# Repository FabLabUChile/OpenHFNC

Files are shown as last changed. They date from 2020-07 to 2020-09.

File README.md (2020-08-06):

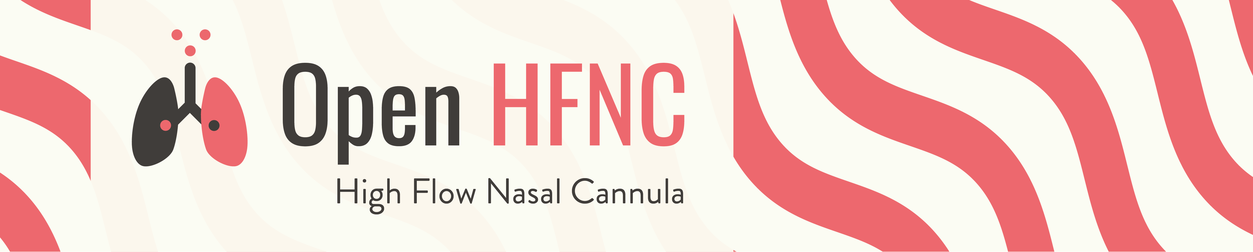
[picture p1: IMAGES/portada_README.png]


# OpenHFNC, Low-Cost Open-Source Alternative Device for High Flow Nasal Therapy
Open Source High Flow Nasal Cannula (Sistema de Terapia Nasal de Alto Flujo de Código Abierto) 

Last update 2020/07/09

### WARNING/DISCLAIMER: We cannot recommend the use of this device on medical applications since it has not been extensively proven. In this project our focus is on reporting the current performance of the device and sharing knowledge that can be used for the development of alternative equipment that can be used in the context of COVID 19. At the current stage this device does not meet all all technical requirements, however we meet some technical requirements that are important. Any further development must be acompanied with the supervision of medical experts. There is a significan risk associated with the inapropiate use of any medical equipment and precautions must be followed. 

Acknowledgements: We thank the collaboration of many profesionals, specially those from the Hospital Clinico Universidad de Chile and also expert advice from professionals from the Pontificia Universidad Catolica de Chile. Through the development of this project we have shared experience and knowledge about the funcioning of several components. 

### ADDITIONAL WARNINGS: This device has not been tested to meet any FDA regulation and has not been certified. 

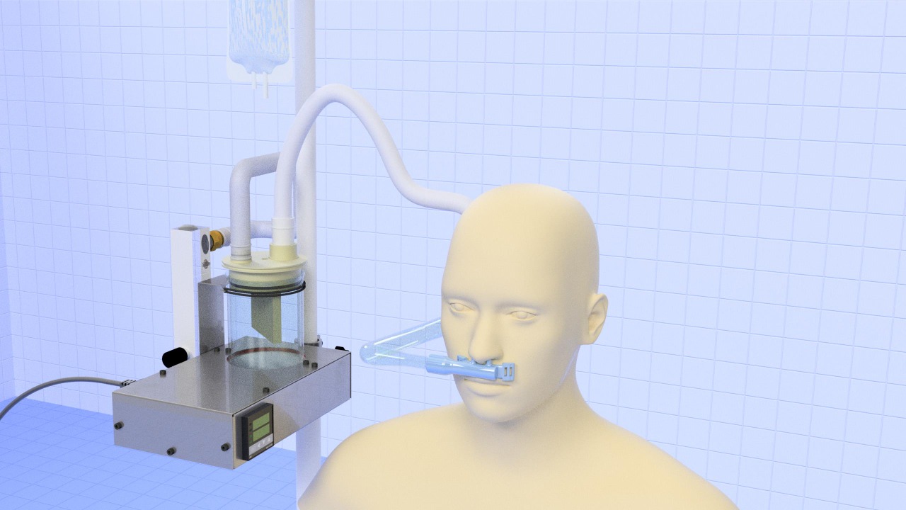
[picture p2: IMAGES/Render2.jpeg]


### MOTIVATION

High Flow Nasal Therapy is an alternative treatment for CODVID 19 patients. Implementing a HFNT device seems less complicated and less expensive than implementing a mechanical ventilator. Moreover it has been reported that HFNT produces less colateral damage to lungs and is also linked with better recovery. 

### TECNICAL REQUIREMENTS

R1. Adjustable Air Flow (Flujo regulable de aire).

The air flow should be in the range of 50 to 70 L/min. 

R2. Mixing Air and Oxygen (Mezcla de Aire y oxígeno en forma regulada).

It should be possible to mix air and oxygen and to regulate the flow of both. Different levels of FiO2 should be
attained. 

R3. Humidification (Humidificación)

Air reaching the patient must be humidified (RH 100%, AH 84 mg/L)

R4. Temperature (Temperatura)

Air must be pre-heated and should reach the patient at a temperature or 37 degrees C. 

R5. Use of heated tube (Uso de tubo calefaccionado)

A pre heated tube must be used to prevent condensation. 

R6. Nasal Cannula (Cánula nasal)

Include a nasal cannula. 

R7. Rapid fabrication.

Implemented ASAP.

R7. Scalability

Several units must be produced. 

### FILE STRUCTURE

* CAD: Design Files of Components.

* BOM: Bill of Materials. 

* ASI: Assembly Instructions. 

* UMA: User Manual. 

* TEC: Technical Evaluation of Performance

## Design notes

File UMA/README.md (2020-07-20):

# USER MANUAL

More information about Instructions for Use DENTAL SG Resine from Formlabs [HERE](https://s3.amazonaws.com/servicecloudassets.formlabs.com/media/Materials/Formlabs+Materials/115000015710-Using+Dental+SG+Resin/DentalSG-Instructions-for-use.pdf)

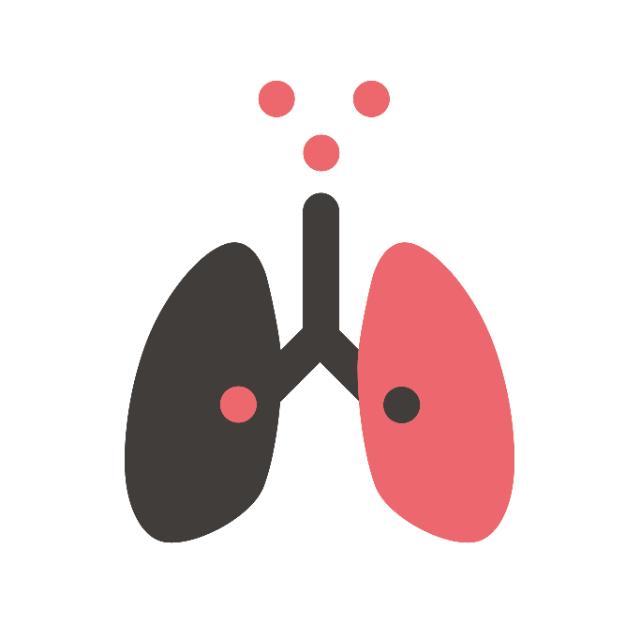
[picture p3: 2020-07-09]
IMAGES/OpenHFNC.jpg

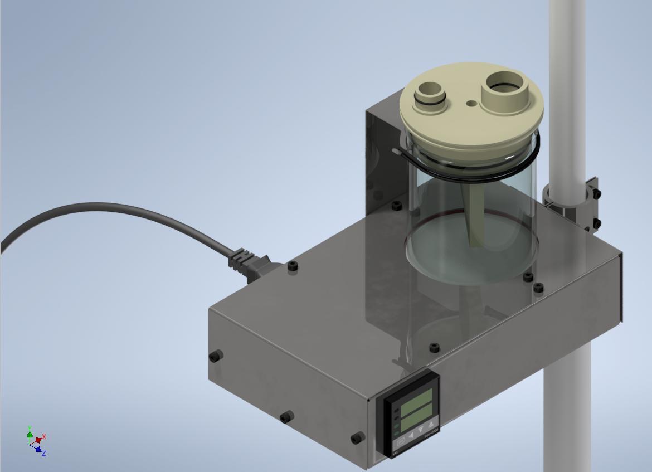
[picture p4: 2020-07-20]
IMAGES/Render1.jpg

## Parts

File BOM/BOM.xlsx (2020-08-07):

Open HFNC | Bill of Materials
System | Subsystem | Part | Quantity | Material | Manufactured or COTS | Description | Reference Sheet in OpenHFNC Manufaturing Drawings |  | COTS - International
Heating-Box | Heating plate box | Box base | 1 | Steel Carbon 1mm thickness | Manufactured | Base of the box that contains the parts that allow the heating of the heating plate and the beaker glass. | Sheet 2 and 3 - DXF file
 |  | Box top | 1 | Steel Carbon 1mm thickness | Manufactured | Cover of the box that contains the parts as descripted above. | Sheet 2 and 4 - DXF File
 |  | M4 rivet nut | 14 |  | COTS | Rivet nut on box base used for linking it with the cover trough the DIN912 M4x10 Screw |  |  | https://www.mcmaster.com/95105A167/ (PENDIENTE, NO ES LA MISMA)
 |  | Heating plate | 1 | Duraluminum | Manufactured | Cirucular plate that receives the heating resistance, distributing the heat, mainly in one of his faces where the beaker glass stands.. | Sheet 2 and 7
 |  | Oring 2-343 Silicone | 1 | Silicone | COTS | Seal that isolates thermal conduction from the heating plate to the top box. Also functions as water leak seal.
 |  | Heater fixing bar | 1 | Alumin | Manufactured | Aluminium bar (125x12x1). Functions as supporting link between the heating plate and the top box. | Sheet 2 and 7
 |  | DIN912 M4x0.7x40-8.8 socket head screw | 2 |  | COTS | DIN912 M4x0.7x40-8.8 socket head screw Holds heater fixing bar to box top |  |  | https://www.mcmaster.com/91290A184/
 |  | DIN 934 M4x0.7 nut | 2 |  | COTS | DIN912 M4x0.7 Nut - Holds heater fixing bar to box top |  |  | https://www.mcmaster.com/90592A090/
 |  | DIN912 M4x0.7x10-8.8 socket head screw | 10 |  | COTS | DIN912 M4x0.7x10-8.8 socket head screw - Secures Box base to box top fitting itself in to M4 Rivet Nut |  |  | https://www.mcmaster.com/91290A144/
 | Electric parts | Thermo couple | 1 |  | COTS | Thermocouple Type K M6 Thread. Measures temperature from Heating plate, REXC100 controller reads it. |  |  | https://www.mpja.com/Thermocouple-Type-K-M6-Threaded-Tip/productinfo/32106%20MI/
 |  | Heater 630W | 1 |  | COTS | Cartridge heater, 220V - 630W. 5/8' DIamater 3' Long. Converts electrical energy in to heat |  |  | https://www.mcmaster.com/35025K473/ (NOTA: IDEALMENTE 630W)
 |  | REXC100 controller | 1 |  | COTS | PID temperature controller.Adjustable Setpoint 0 - 400ºC |  |  | https://www.mcmaster.com/38615K73/ https://www.amazon.com/-/es/REX-C100-48-100-controlador-temperatura/dp/B07KXPLZTQ
 |  | Solid State Relay SSR-25DA | 1 |  | COTS | Solid State Relay; controls current flow to Heater 630W (opening it or closing it) in response to the REXC100 signal |  |  | https://www.amazon.com/Artshu-M%C3%B3dulo-SSR-25DA-entrada-24-380VAC/dp/B07JZF6973/
 |  | On-Off Switch | 1 |  | COTS | On/Off switch for electrical energy, from OpenHFNC team. |  |  | https://www.mcmaster.com/7030K45/
 |  | IEC C14 male panel connector | 1 |  | COTS | C14 male power connector |  | https://altronics.cl/conector-poder-panel-macho-c14?tag=C14 | https://www.amazon.com/Baomain-Panel-Power-Socket-Connector/dp/B00WFYS1HS
 |  | 220 AC power cable | 1 |  | COTS | 220 AC power cable- C14 female power connector |  |  | https://www.mcmaster.com/power-cords/voltage~250v-ac/
 |  | DIN913-M5x5 socket screw flat end | 2 |  | COTS | DIN 913-M5x5 socket screw flat end-Sets heating cartridge to heating box |  |  | https://www.ametric.com/product/85223/m5x5-din-913
 |  | DIN7991 M3x0.5x10-8.8 countersunk head cap screws | 2 |  | COTS | DIN 7991 M3x0.5x10-8.8 countersunk head cap screw.Sets panel connector C14 to top box |  |  | https://www.mcmaster.com/91294A130/
 |  | DIN 934 M3 nut | 2 |  | COTS | DIN934 M3x0.5 nut. Sets Panel C14 power connector to top box. |  |  | https://www.mcmaster.com/90592A085/
 | Glass vase & flow meter fixer | Glass fixer plate | 1 | Steel Carbon 1mm thickness | Manufactured | Plaque that is set to heating plate and allows the beaker glass and the flowmeter to stay in place. | Sheet 2 and 5 - DXF file |  | -
 |  | DIN912 M4x0.7x10-8.8 socket head screw | 2 |  | COTS | DIN912 M4x0.7x10-8.8 socket head screw - Sets the glass fixer plate to the heating box. |  |  | https://www.mcmaster.com/91290A144/
 |  | Oring 2-159 | 1 | Nitrile | COTS | Oring that functions as elastic band between beaker glass and the glass fixer plate.
 | IV stand fixer | IV stand fixer plate | 2 | Steel Carbon 1mm thickness and A53 Pipe | Manufactured | Plaque that is set to the heating box and allows in his other end to be fixed to the IV stand. | Sheet 2 and 6 - DXF file
 |  | Star knob 1/4 UNC | 1 |  | COTS | Star Knob 1/4-20UNC. For stand fixer plate to IV stand fixation |  |  | https://www.amazon.com/Big-Horn-19707B-5PK-Star-Thru/dp/B01DO22H5Q?c=ts&s=industrial&ts_id=16412791
 |  | DIN912 M4x0.7x10-8.8 socket head screw | 6 |  | COTS | DIN912 M4x0.7x10-8.8 socket head screw - (4) are for setting the stand fixer plate to heating box. (2) are for attaching both stand fixer plates. |  |  | https://www.mcmaster.com/91290A144/
 |  | DIN 934 M4 nut | 2 |  | COTS | DIN 934 M4x0.7 Nut.Used for attaching both stand fixer plates. |  |  | https://www.mcmaster.com/91415A020/
 |  | Split washer DIN 124B D4 | 2 |  | COTS | DIN 124B Split Washer Inner diameter 4mm.Used for attaching both stand fixer plates.
Ventilation pipeline | Flow pipelines | LZM-15ZT flowmeter | 1 |  | COTS | Flowmeter 10-100 LPM (0.6-6 m3N/h) - Conections G1/4 BSP female and G1/2 BSP male, both for inlet and outlet |  |  | https://www.grainger.com/product/BROOKS-10-to-100-lpm-Variable-Area-16X857
 |  | Corrugated tube | 1 |  | COTS | Tube that carries air/oxygen flow from flowmeter to the beaker glass.
 |  | Heated tube | 1 |  | COTS | Heated tube that carries air/oxygen humidified flow from beaker glass to transfer tube. |  |  | https://www.directhomemedical.com/HBT300-hybernite-heated-cpap-hose-tube.html
 |  | Transfer tube | 1 |  | COTS | Tube that carries air/oxygen flow from heated tube to nasal cannula. .Also serves as flow area smooth reduction tube between the components at his ends. |  |  | https://www.amazon.com/Hand-Drum-Pump-Siphon-Polyethylene/dp/B00ZZY2EFU Dukshin, Siphon Hand Pump (Product Number: DP-14)
 |  | Conical rubber stopper 12mm | 1 |  | COTS | Rubber stopper (9,5×12,5-17,5). Plug a hole of transfer tube to adapt this item for ventilation pipeline |  |  | https://www.mcmaster.com/9545K113-9545K11/
 |  | BSP 1/4 - Hose 7/8 | TBD |  | COTS | Fitting Connection between flowmeter output and corrugated tube
 |  | BSP 1/4 - Hose 1/4 | TBD |  | COTS | Fitting Connection between 1/4' high flow medical tube and flowmeter input |  |  | https://www.mcmaster.com/1075T22/
 |  | Y conection | TBD |  | COTS | Y connector that receives air and oxygen and delivers to both 1/4' high flow medical tubes.
 |  |  | TBD |  | COTS
 | Beaker glass - Top connectors | Beaker glass 600ml, diam: 90mm | 1 |  | COTS | Beaker Glass 600ml diameter 90mm. For distilled water. Receives heat coming from the heating plate.Where water evaporation for air/oxygen flow humidification occurs. |  |  | https://www.duran-group.com/en/produkte-loesungen/laborglas/produkte/kochglaeser-allgemeines-laborglas/becher.html - Cat. No.: 21 106 48
 |  | Top lid body | 1 | Polypropylene | Manufactured | Beaker glass top lid body. Seals the gaps and create connections for the heating tube (oulet flow) and corrugated tube (inlet flow) | Sheet 8 and 9
 |  | Heated tube-top lid connector | 1 | Polypropylene | Manufactured | Connector between heating tube and top lid body. | Sheet 8 and 10
 |  | Corrugated tube-top lid connector | 1 | Polypropylene | Manufactured | Connector between corrugated tube and top lid body | Sheet 8 and 10
 |  | Paddle | 1 | Polypropylene | Manufactured | Paddle that provides separation inside the beaker glass and allows the entering flow to moisturize by forcing it to pass near water in evaporation process . | Sheet 8 and 11
 |  | DIN 912 M4x16 | 1 | Stainless steel | COTS | DIN912 M4x0.7x40-8.8 socket head screw -Sets Paddle to Top Lid Body |  |  | https://www.mcmaster.com/91290A154/
 |  | Oring 2-007 | 1 | Nitrile | COTS | Seal between paddle and top lid body
 |  | Oring 2-018 | 1 | Nitrile | COTS | Seal between corrugated tube amd top lid connector
 |  | Oring 2-019 | 1 | Nitrile | COTS | Seal between corrugated tube-top lid connector and top lid body
 |  | Oring 2-022 | 1 | Nitrile | COTS | Seal between heated tube-top lid connector and heated tube
 |  | Oring 2-026 | 1 | Nitrile | COTS | Seal between heated tube-top lid connector and top lid body
 |  | Oring 2-151 | 1 | Nitrile | COTS | Seal between top lid body and beaker glass
 | Nasal cannula | Nasal cannula body | 1 | Dental SG Resin | Manufactured | BIocompatible 3D printed nasal cannula Delivers humidified air/oxygen flow to the patient through his nostrils. | STEP and STL File
 |  | Oring 2-014 | 1 | Nitrile | COTS | Seal between nasal cannula body and transfer tube
 |  | Elastic band | TBD how many meters |  | COTS | Elastic band used to hold nasal cannula to the patients head.

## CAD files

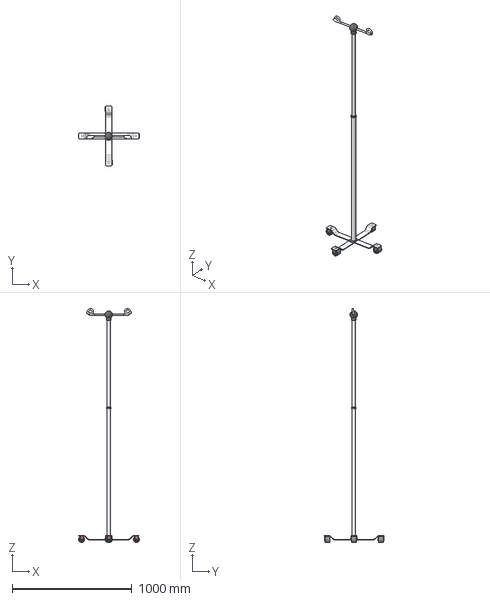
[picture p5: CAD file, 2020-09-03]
CAD/Step/Auxiliary Components/IV Stand.stp
508.6 x 502.9 x 1955.7 mm

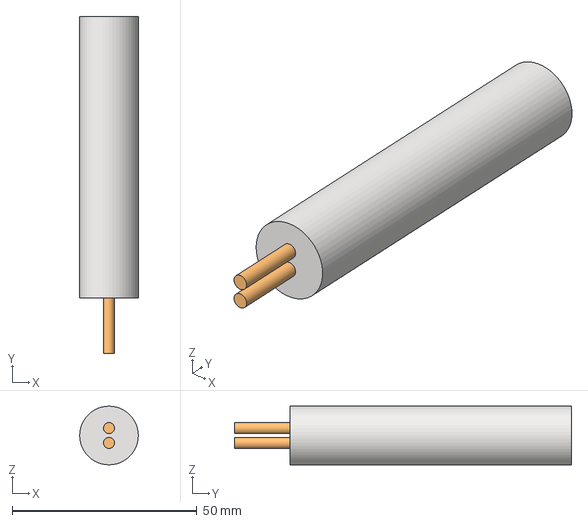
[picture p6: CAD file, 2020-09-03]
CAD/Step/Heating Box/Electric Parts/Heater630W.stp
15.9 x 91.2 x 15.9 mm

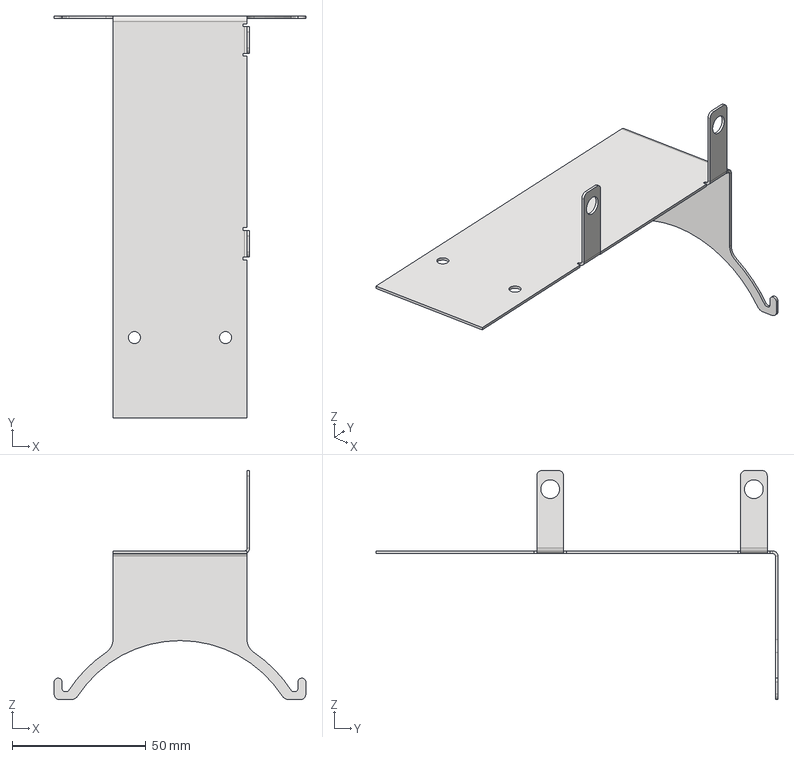
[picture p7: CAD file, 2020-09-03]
CAD/Step/Heating Box/Glass vase _ flow meter fixer/Glass fixer plate.stp
93.9 x 150.0 x 85.5 mm

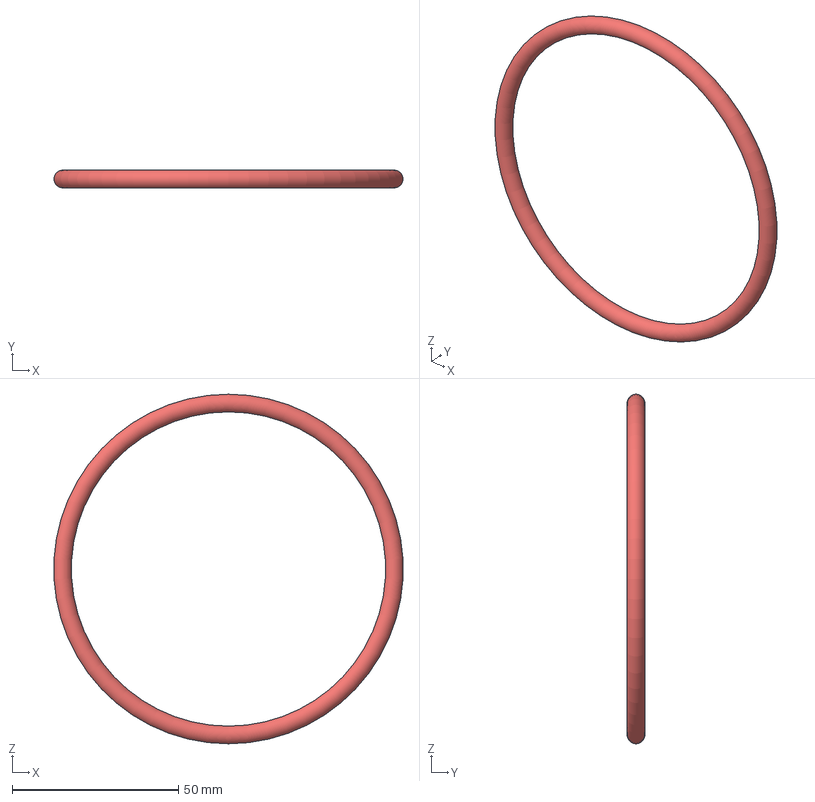
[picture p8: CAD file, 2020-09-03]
CAD/Step/Heating Box/Heating plate box/Oring 2-343 Silicone.stp
105.1 x 5.33 x 105.3 mm

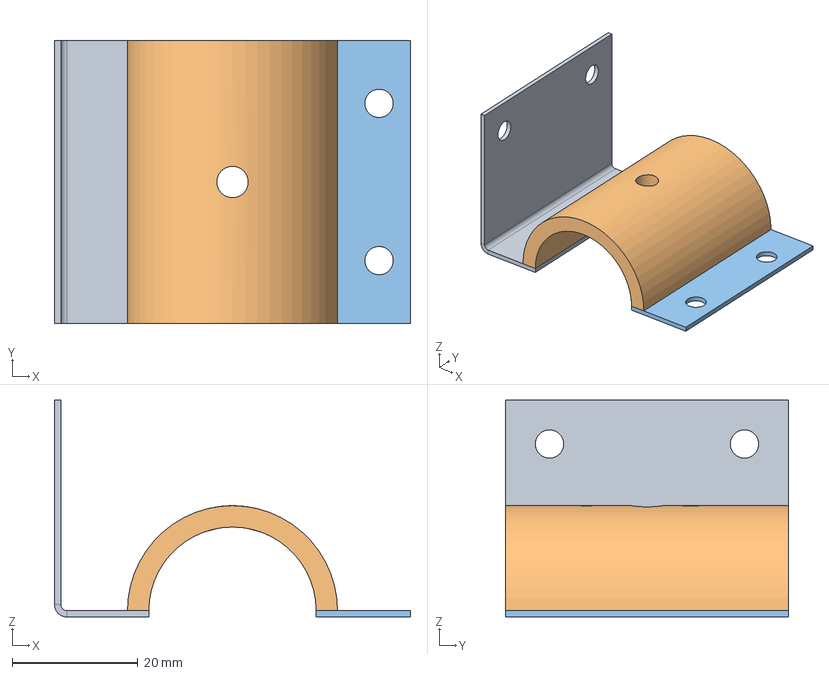
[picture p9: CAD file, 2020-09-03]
CAD/Step/Heating Box/IV stand fixer/IV stand fixer plate.stp
56.6 x 45.0 x 34.5 mm

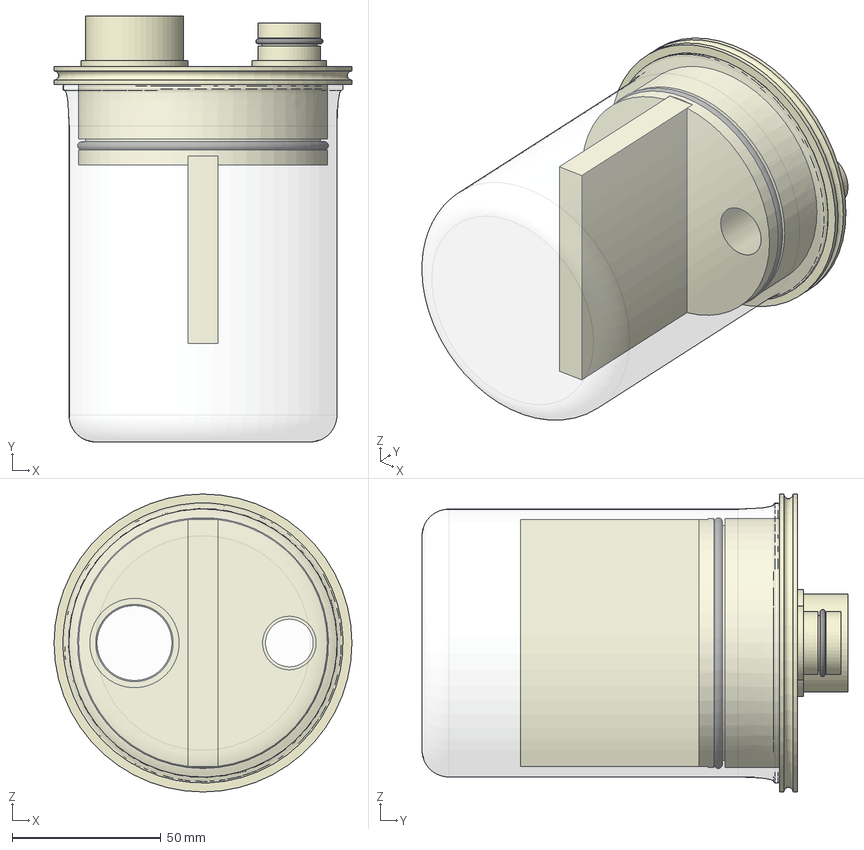
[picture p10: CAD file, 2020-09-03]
CAD/Step/Ventilation pipeline/Beaker glass - top connector.stp
100.0 x 143.0 x 100.0 mm
Precipitated Glass 600ml-De90-Di84-H120
Body glass top
Paddle
Oring 2-007
DIN912 M4x0.7x16-8.8 socket head screw
Oring 2-026
Oring 2-019
Oring 2-151 Deform
Corrugated-top connector
Heated tube-top connector
Oring 2-018 Deform
Oring 2-022

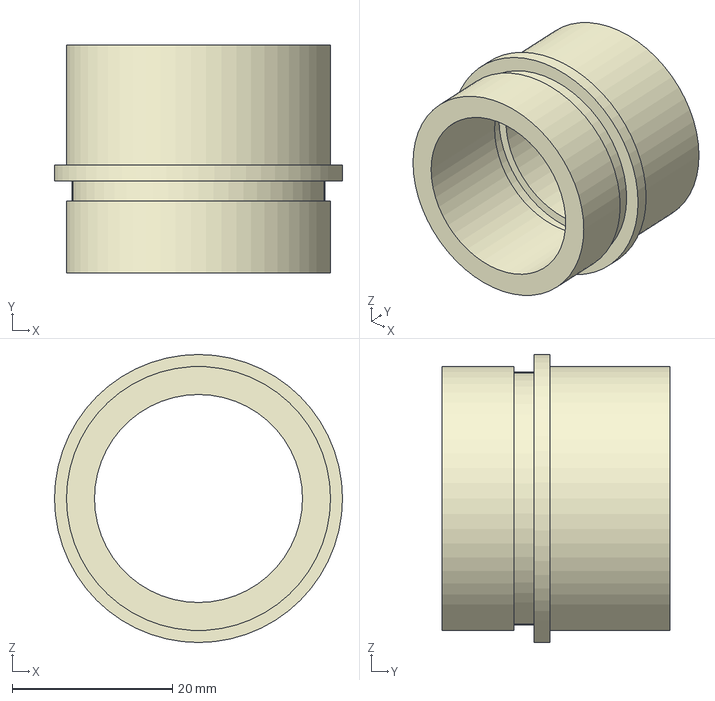
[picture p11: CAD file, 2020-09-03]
CAD/Step/Ventilation pipeline/Beaker glass - top connector/Heated tube-top lid connector.stp
36.0 x 28.5 x 36.0 mm

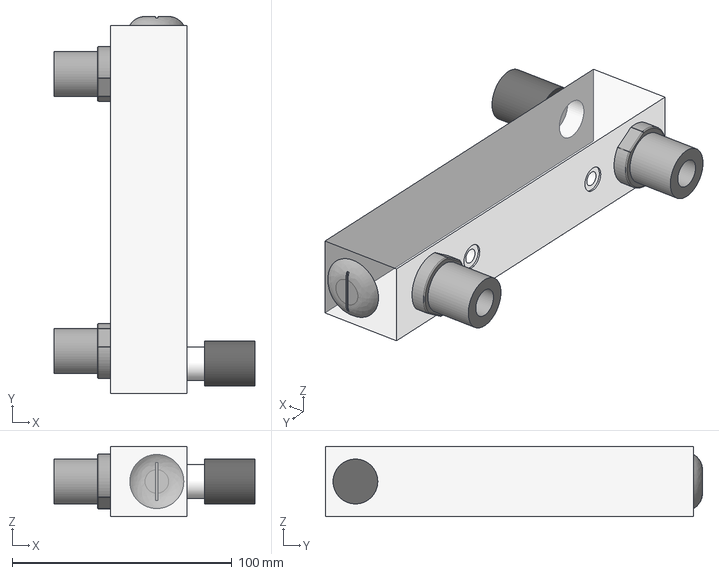
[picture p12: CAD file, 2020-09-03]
CAD/Step/Ventilation pipeline/Flow pipelines/LZM-15ZT flowmeter parts/LZM-15ZT_rotameter_06-6_M3-H.stp
91.5 x 171.7 x 31.9 mm

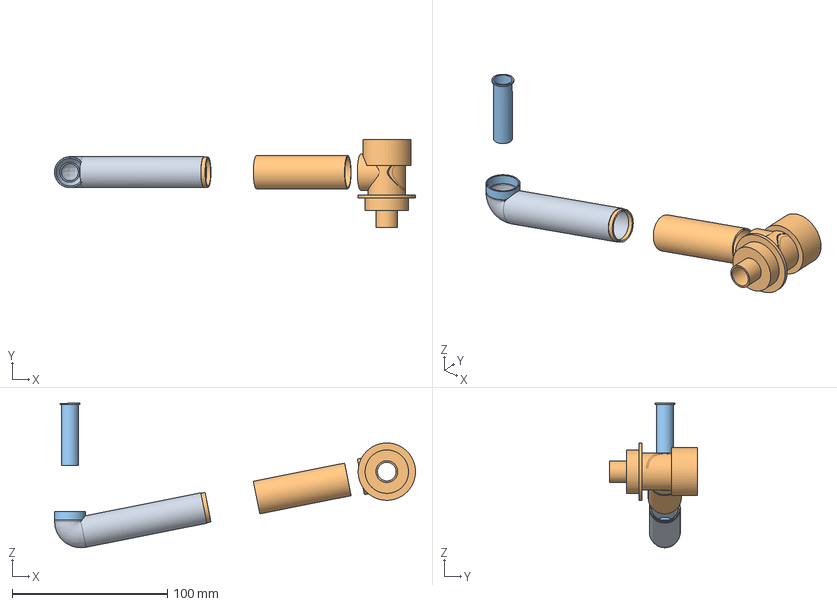
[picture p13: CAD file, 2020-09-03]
CAD/Step/Ventilation pipeline/Flow pipelines/Transfer tube (bended version).stp
232.7 x 57.0 x 93.2 mm

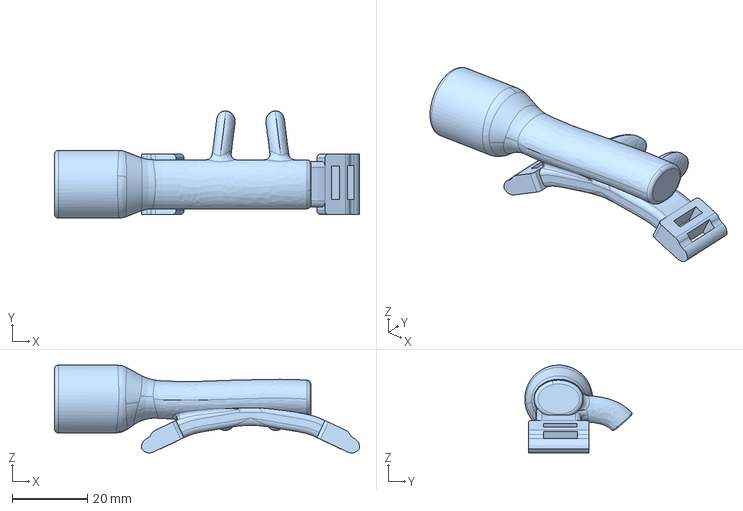
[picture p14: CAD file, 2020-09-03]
CAD/Step/Ventilation pipeline/Nasal cannula/Nasal Cannula.stp
80.9 x 28.5 x 23.3 mm

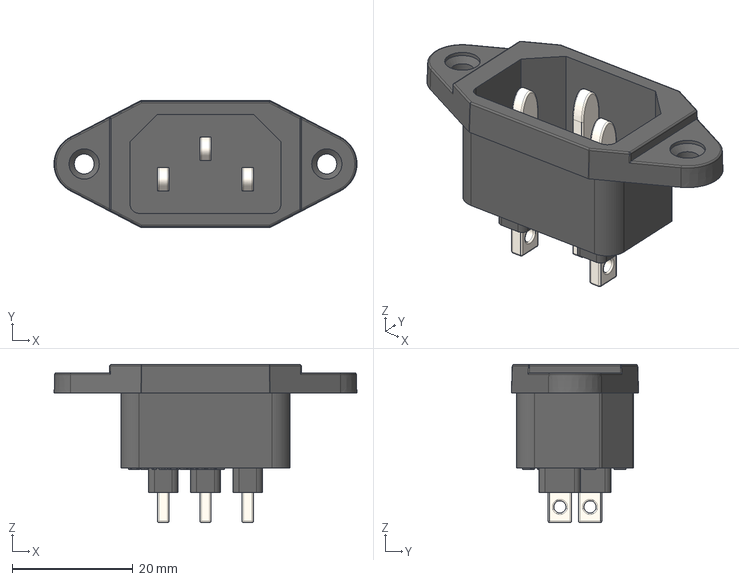
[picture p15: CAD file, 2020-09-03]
CAD/Step/Heating Box/Electric Parts/IEC C14 Male panel connector.stp
50.2 x 21.1 x 26.2 mm

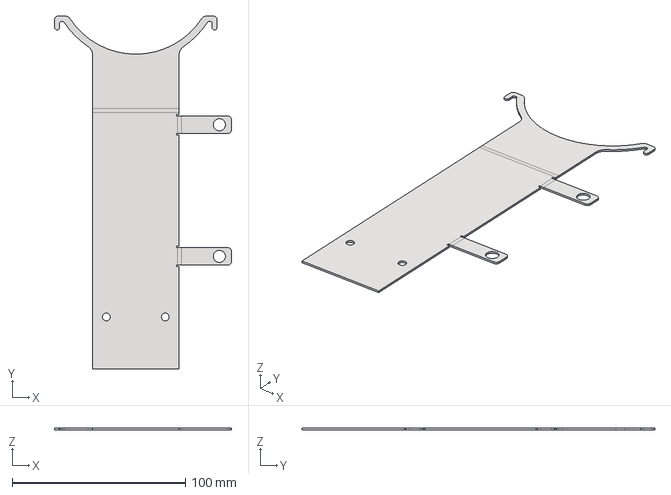
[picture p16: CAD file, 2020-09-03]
CAD/Step/Heating Box/Glass vase _ flow meter fixer/Glass fixer plate_extended.stp
102.2 x 203.8 x 1.00 mm

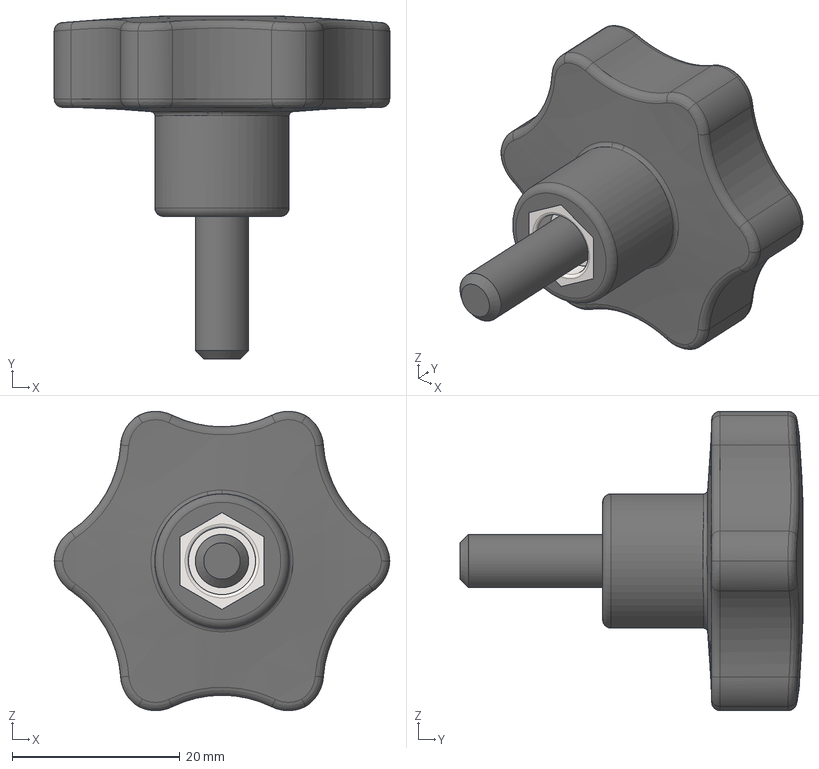
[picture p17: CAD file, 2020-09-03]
CAD/Step/Heating Box/IV stand fixer/Star Knob 1-4UNC.stp
40.0 x 40.9 x 35.7 mm

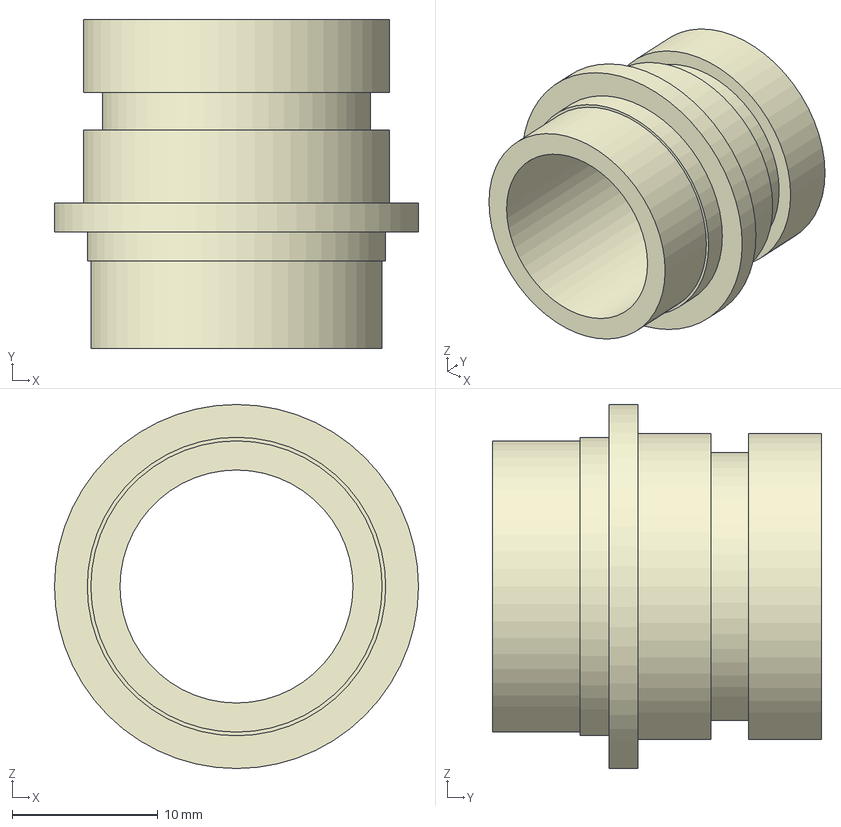
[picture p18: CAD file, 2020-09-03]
CAD/Step/Ventilation pipeline/Beaker glass - top connector/Corrugated tube-top lid connector.stp
25.0 x 22.6 x 25.0 mm

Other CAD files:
CAD/Step/Ventilation pipeline/Flow pipelines/LZM-15ZT flowmeter.stp
CAD/Step/Ventilation pipeline/Nasal cannula/Oring 2-014.stp
CAD/Step/Ventilation pipeline/Beaker glass - top connector/Beaker glass 600ml, diam_ 90mm.stp
CAD/Inventor/Auxiliary Components/IV Stand.ipt
CAD/Inventor/For ASI/OldVersions/ToASI-0A.0001.iam
CAD/Inventor/For ASI/OldVersions/ToASI-0B.0003.iam
CAD/Inventor/For ASI/OldVersions/ToASI-1.0002.iam
CAD/Inventor/For ASI/OldVersions/ToASI-2.0003.iam
CAD/Inventor/For ASI/OldVersions/ToASI-3.0001.iam
CAD/Inventor/For ASI/OldVersions/ToASI-4.0001.iam
CAD/Inventor/For ASI/OldVersions/ToASI-5.0001.iam
CAD/Inventor/For ASI/OldVersions/ToASI-6.0001.iam
CAD/Inventor/For ASI/ToASI-0A.iam
CAD/Inventor/For ASI/ToASI-0B.iam
CAD/Inventor/For ASI/ToASI-1.iam
CAD/Inventor/For ASI/ToASI-2.iam
CAD/Inventor/For ASI/ToASI-3.iam
CAD/Inventor/For ASI/ToASI-4.iam
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

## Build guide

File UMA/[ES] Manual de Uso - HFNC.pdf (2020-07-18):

# High Flow Nasal Cannula

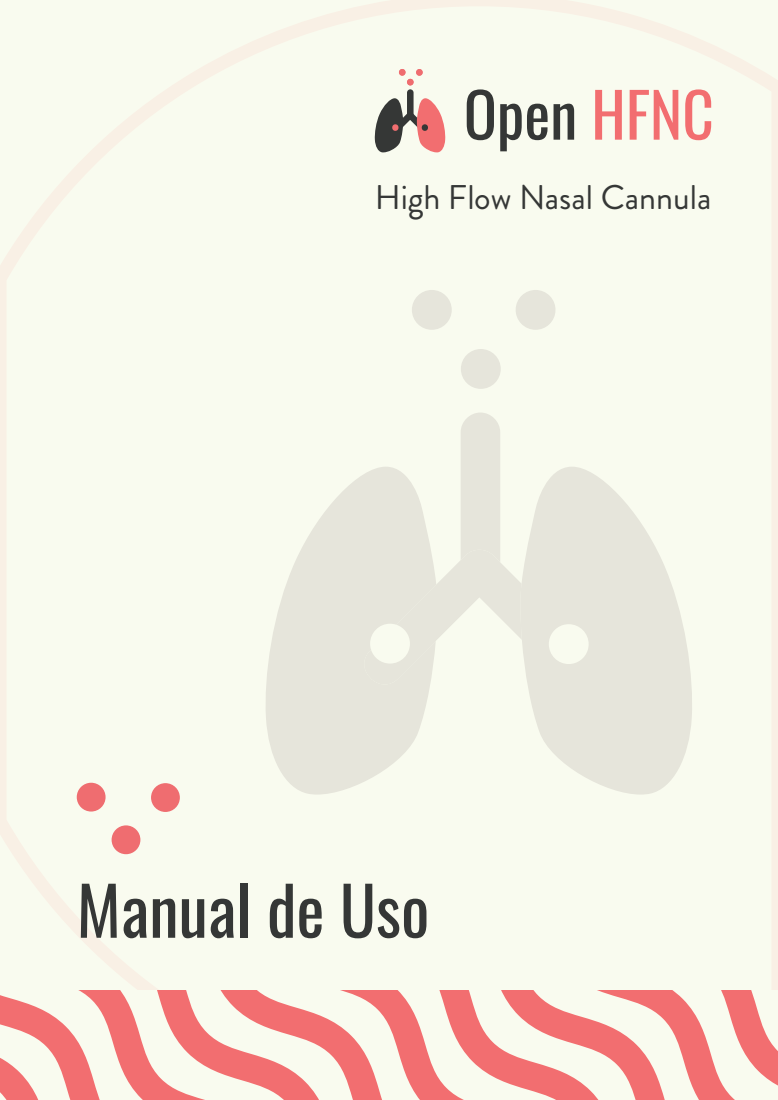
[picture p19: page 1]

# Open HFNC

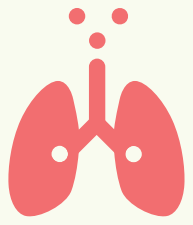
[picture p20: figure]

El dispositivo Open High Flow Nasal Cannula intenta usarse para el desarrollo de equipos alternativos que pueden emplearse en el contexto de COVID 19.

El dispositivo ha sido desarrollado en el menor tiempo posible. No ha sido posible generar pruebas en personas en estado crítico ni un amplio testeo para validar con exactitud eventualidades particulares.

Este es un proyecto realizado en la Universidad de Chile por un equipo de ingenieros y consultando constantemente a personal médico para validar los materiales y su funcionamiento.

Agradecemos la colaboración de muchos profesionales, especialmente los del Hospital Clínico Universidad de Chile y también el asesoramiento experto de profesionales de la Pontificia Universidad Católica de Chile. A través del desarrollo de este proyecto, hemos compartido experiencias y conocimientos sobre el funcionamiento de varios componentes.

El proyecto es Open Hardware y puede encontrarse en GitHub.

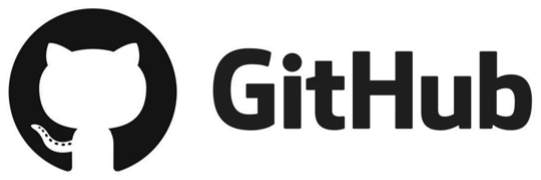
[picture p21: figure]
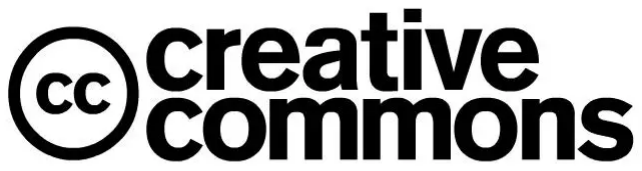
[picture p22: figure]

Uso Previsto | La cánula nasal Open HFNC es una cánula nasal diseñada
| para administrar un tratamiento nasal de flujo alto calentado y humidificado a pacientes con respiración espontánea que necesitan apoyo para respirar. Este producto está diseñado para su uso en entornos hospitalarios y debe ser bajo supervisión de personal médico.

# Advertencias Generales

| • El dispositivo ha sido desarrollado en el menor tiempo posible. NO ha sido posible generar pruebas en personas en estado crítico ni un amplio testeo para validar con exactitud eventualidades particulares. • Su uso debe realizarse de acuerdo a las regulaciones de cada país. NO podemos certificar su uso correcto. • Este producto sólo está diseñado y verificado bajo requisitos técnicos para utilizarse con las piezas particulares del mismo. La interacción con otros repuestos comerciales y no comerciales puede alterar su rendimiento y ocasionar resultados no previstos. • Es necesario supervisar constantemente al paciente para evitar situaciones como la saturación de oxígeno, elevadas temperaturas y otros, podría ocasionar daños graves.

# Precauciones Generales

| • NO reutilice la cánula sin su esterilización previa. Su reutilización inapropiada puede causar la transmisión de sustancias infecciosas, la interrupción del tratamiento, daños graves. • Asegúrese que los tubos no se encuentren enredados o estrangulados, ni con el paciente, ni entre este mismo. • NO utilice el producto en el caso que alguna pieza se encuentre alterado o quebrado.
Motivación | La terapia nasal de alto flujo (HFNT) es un tratamiento
| alternativo para los pacientes con CODVID 19. Implementar un dispositivo HFNT parece menos complicado y menos costoso que implementar un ventilador mecánico. Además, se ha informado que HFNT produce menos daño colateral a los pulmones y también está relacionado con una mejor recuperación*.

* The use of high - flow nasal oxygen in COVID - 19 https://onlinelibrary.wiley.com/doi/full/10.1111/anae.15073

# Open HFNC

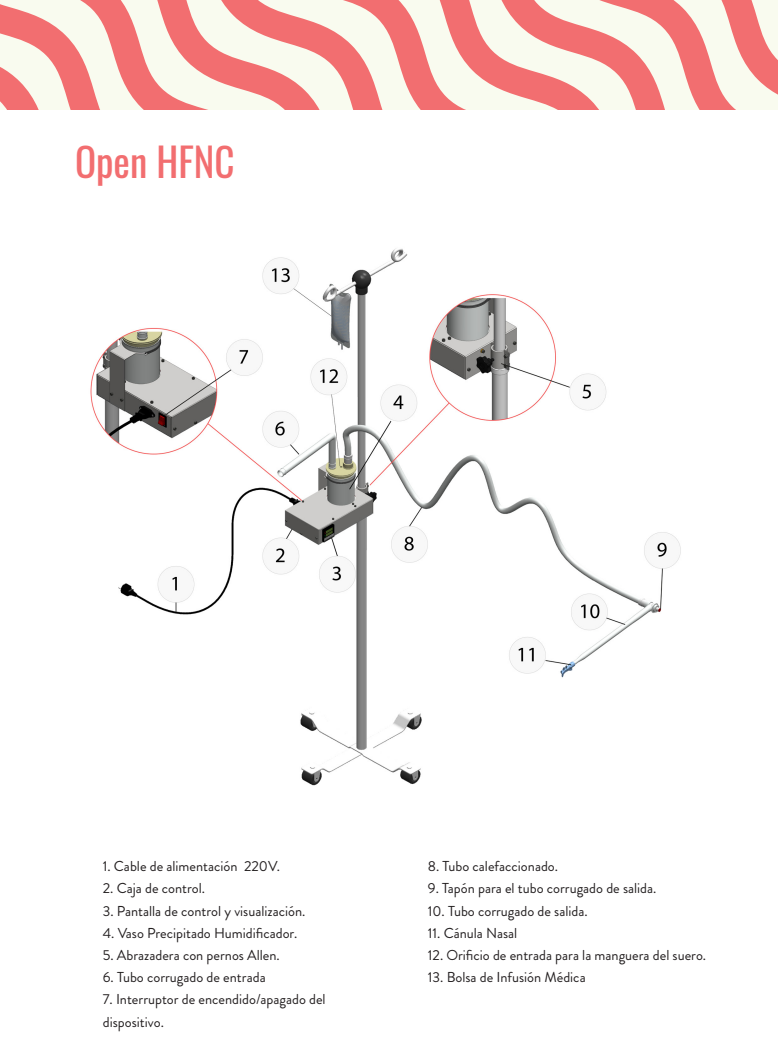
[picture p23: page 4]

1. Cable de alimentación 220V.
2. Caja de control.
3. Pantalla de control y visualización.
4. Vaso Precipitado Humidificador.
5. Abrazadera con pernos Allen.
6. Tubo corrugado de entrada
7. Interruptor de encendido/apagado del
dispositivo.

8. Tubo calefaccionado.
9. Tapón para el tubo corrugado de salida.
10. Tubo corrugado de salida.
11. Cánula Nasal
12. Orificio de entrada para la manguera del suero.
13. Bolsa de Infusión Médica

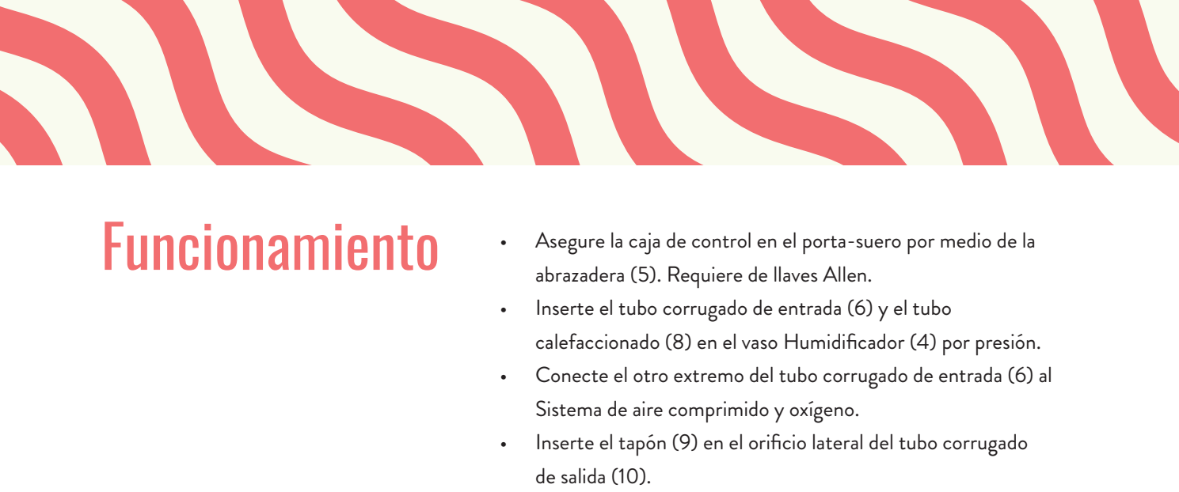
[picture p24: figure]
Sistema de aire comprimido y oxígeno.; de salida (10).

Funcionamiento • Asegure la caja de control en el porta-suero por medio de la

abrazadera (5). Requiere de llaves Allen.
- Inserte el tubo corrugado de entrada (6) y el tubo calefaccionado (8) en el vaso Humidificador (4) por presión.
- Conecte el otro extremo del tubo corrugado de entrada (6) al
- Inserte el tapón (9) en el orificio lateral del tubo corrugado
- Conecte el extremo del tubo calefaccionado (8) con el tubo corrugado de salida (10) por presión.
- Conecte por presión la cánula nasal (11) con el tubo corrugado de salida (10).
- Llene la bolsa de infusión médica (13) con agua.
- Conecte la manguera saliente de la bolsa de infusión médica
(13) al orificio del vaso humidifcador (4) para llenarlo de agua paulatinamente hasta los 100mL que indica el mismo vaso precipitado.
- Encienda el equipo y automáticamente el plato calefactor empezará a calentar. Observará en la pantalla de control
(3) la temperatura configurada y la temperatura actual. Esta última deberá avanzar hasta llegar a la temperatura configurada.

# Requerimientos Técnicos

Flujo de aire ajustable
- El flujo de aire debe estar en el rango de 50 a 70 L/min.

Mezcla de aire y oxígeno
- Debe ser posible mezclar aire y oxígeno y regular el flujo de ambos. Se deben alcanzar diferentes niveles de FiO2.

Humidificación
- El aire que llega al paciente debe ser humidificado (HR 100%, AH 84 mg / L)

Temperatura
- El aire debe precalentarse y debe llegar al paciente a una temperatura de 37 ºC.

Uso de tubo calentado
- Usar un tubo precalentado para evitar la condensación.

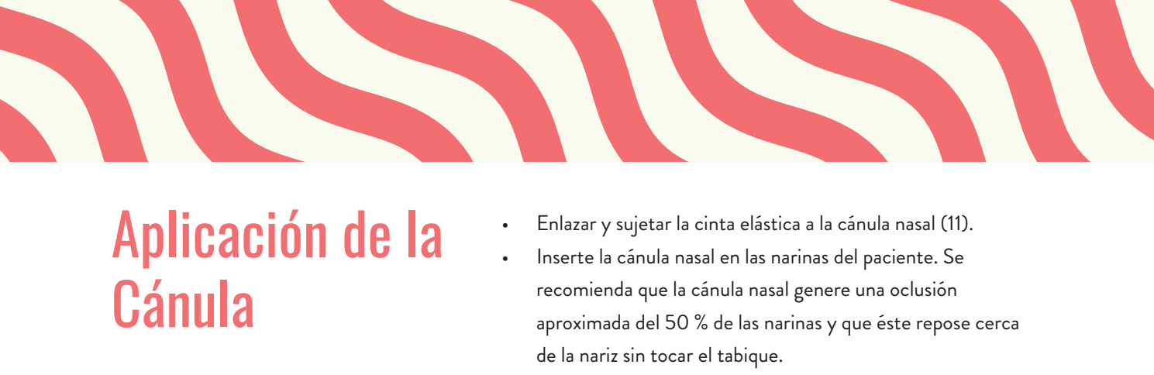
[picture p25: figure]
Aplicación de la Cánula; de la nariz sin tocar el tabique.
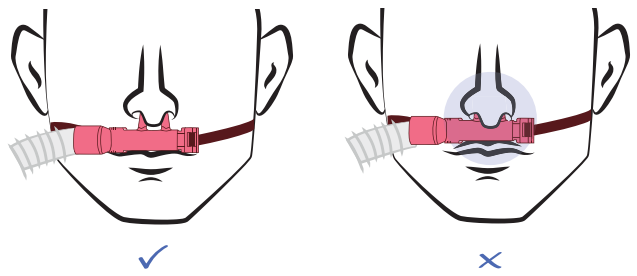
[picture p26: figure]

Precauciones | • NO envuelva, aísle, estire ni aplaste los tubos, ya
| que podría verse perjudicado el rendimiento de este dispositivo, es posible que se causen daños graves al paciente y/o se presente fallos en el funcionamiento del equipo. • Vigile la condensación para evitar la oclusión o la acumulación de fluido. Extraiga los fluidos del paciente según sea necesario.

# Extracción de la cánula

La cánula nasal está fabricado por un material biocompatible permitiendo que ésta pueda ser reutilizado después de una esterilización correspondiente.

- Retire la cánula con cuidado y debe proceder a desinfectarlo y esterilizarlo (vea la siguiente sección).
- Desinfecte y esterilice la cinta elástica.
- Enlazar y sujetar la cinta elástica a la cánula nasal (11).
- Inserte la cánula nasal en las narinas del paciente. Se recomienda que la cánula nasal genere una oclusión aproximada del 50 % de las narinas y que éste repose cerca

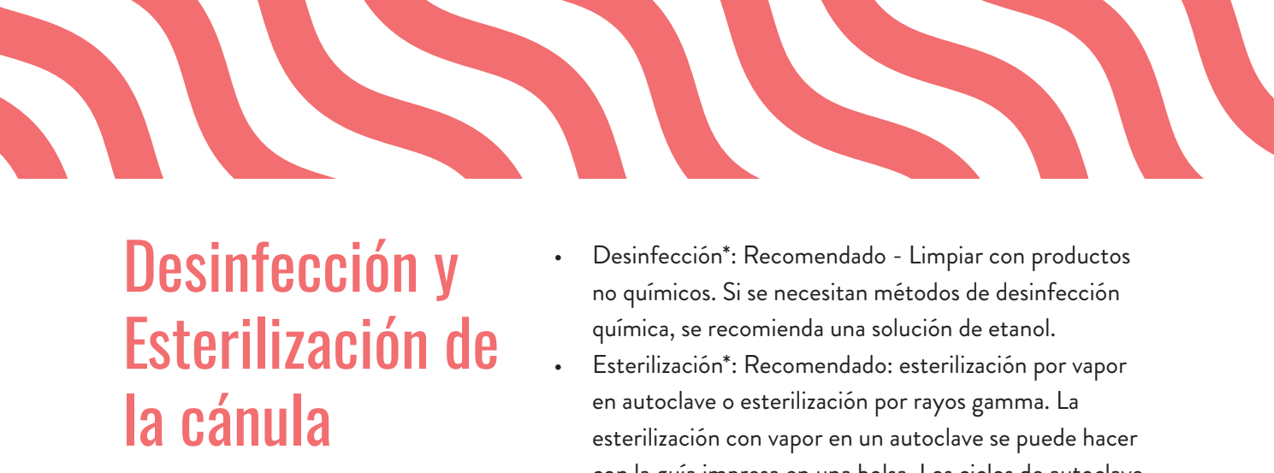
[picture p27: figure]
Desinfección y Esterilización de la cánula

# Especificaciones Técnicas

- La cánula nasal está fabricada con la resina biocompatible Dental SG Resin
- El aire debe precalentarse y llegar al paciente a una temperatura de 37º C.
- Se debe usar un tubo precalentado para evitar la condensación.
- Desinfección*: Recomendado - Limpiar con productos no químicos. Si se necesitan métodos de desinfección química, se recomienda una solución de etanol.
- Esterilización*: Recomendado: esterilización por vapor en autoclave o esterilización por rayos gamma. La esterilización con vapor en un autoclave se puede hacer con la guía impresa en una bolsa. Los ciclos de autoclave recomendados son 15 minutos a 121 ° C o 3 minutos a 138 ° C.

* Información extraída de INSTRUCCIONES DE USO DENTAL SG de Formlabs https://support.formlabs.com/

# Componentes Desechables

- Los materiales que pueden soportar hasta 120ºC pueden ser reutilizadas luego de su procedimiento de desinfección y esterilización correspondiente. Por esta razón, el tubo corrugado de entrada (6), tubo corrugado de salida (10) y el tapón (9) SON DESECHABLES.

## El equipo:

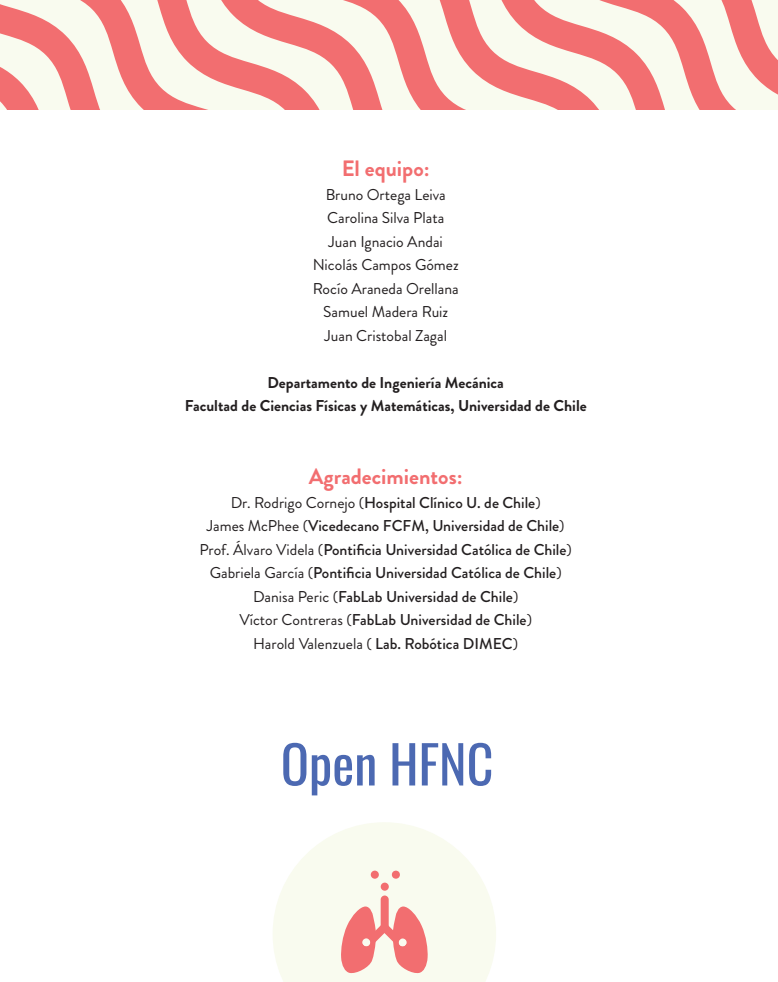
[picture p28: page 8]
Agradecimientos:

Bruno Ortega Leiva
Carolina Silva Plata
Juan Ignacio Andai
Nicolás Campos Gómez
Rocío Araneda Orellana
Samuel Madera Ruiz
Juan Cristobal Zagal

Departamento de Ingeniería Mecánica

Facultad de Ciencias Físicas y Matemáticas, Universidad de Chile

Dr. Rodrigo Cornejo (Hospital Clínico U. de Chile)
James McPhee (Vicedecano FCFM, Universidad de Chile)
Prof. Álvaro Videla (Pontificia Universidad Católica de Chile)
Gabriela García (Pontificia Universidad Católica de Chile)
Danisa Peric (FabLab Universidad de Chile)
Víctor Contreras (FabLab Universidad de Chile)
Harold Valenzuela ( Lab. Robótica DIMEC)
Open HFNC

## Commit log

2020-07-14 Agrega archivos CAD
    [AC plug.ipt, Adaptador_inflador_corrugadoscf.ipt, Adaptador_inflador_corrugadoscf.stl, Adaptador_inflador_corrugadoscf.stp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]
2020-07-17 file renaming
    [AC plug.ipt, Adaptador_inflador_corrugadoscf.ipt, Adaptador_inflador_corrugadoscf.stl, Adaptador_inflador_corrugadoscf.stp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]
2020-07-27 Added central CAD assembly
    [AC plug.ipt, Assembly129.0001.iam, Assembly129.iam, Assembly129_1.0001.iam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]
2020-07-29 added BOM and Rotameter CAD model
    [BOM.xlsx, LZM-15ZT_rotameter_06-6_M3-H.ipt, LZM-15ZT_rotameter_06-6_M3-H.stp, LZM-15ZT_rotameter_06-6_M3-H_Assembly.iam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]
2020-08-06 Bill of Materials update
    [BOM.xlsx, PIDsupport.0004.ipt, PIDsupport.ipt, PIDsupport.stl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]
2020-08-07 CAD files update
    [220 AC power cable.ipt, 2306_canula_5.SLDPRT, 2306_canula_5.STL, AC plug.ipt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]
2020-09-03 ADD: STEP CAD files
    [220 AC power cable.stp, Beaker glass - top connector.iam, Beaker glass - top connector.ipn, Beaker glass - top connector.stp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]
